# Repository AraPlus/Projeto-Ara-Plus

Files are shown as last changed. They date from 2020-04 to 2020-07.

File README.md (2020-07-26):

# Projeto-Ara-Plus
Repositório de projeto de um AMBU automatizado desenvolvido por estudantes, pesquisadores e professores da Universidade Federal do ABC (UFABC) para substituir um ventilador pulmonar de forma emergencial nos casos de COVID-19. Este é um trabalho em desenvolvimento, e ainda não está apto para casos clínicos. Futuras atualizações devem ser lançadas em breve.

## Origem do Nome
O nome "Ara" vem do Tupi-Guarani e significa "ar". Portanto o nome Ara-Plus reune uma palava genuinamente brasileira com uma palavra do inglês reconhecida em todo o mundo, significando literalmente "mais ar".

## Descrição geral do sistema

### Requisitos

Conforme destacado pela AMIB – [Associação de Medicina Intensiva Brasileira]() – em sua nota técnica ["Nota técnica sobre características de aparelhos ventiladores artificiais no suporte ao paciente com COVID-19"](http://www.amib.org.br/fileadmin/user_upload/amib/2020/abril/26/Nota_te__cnica_sobre_caracteri__sticas_de_aparelhos_ventiladores_artificiais_no_suporte_ao_paciente_com_COVID-19.pdf) de 26 de abril de 2020 e que atualmente (29/05/2020) subsidia o [PROJETO DE LEI N° 2294, DE 2020, em tramitação no senado,](https://www25.senado.leg.br/web/atividade/materias/-/materia/142132): "No atual cenário de pandemia por COVID-19, diante de uma situação de exceção decorrente do grande número de pacientes com necessidade de ventilação mecânica, listamos abaixo as especificações MÍNIMAS que um ventilador mecânico deve apresentar para ventilar pacientes com COVID-19, em qualquer unidade (pronto socorro, UTI ou outras unidades). Essas características devem estar presentes, independentemente de o equipamento ser ventilador de transporte ou não, ser novo ou reformado:
1. MODOS VCV e/ou PCV;
2. CONTROLE DE DELTA DE PRESSÃO (SOBRE A PEEP) NO MODO PCV (DE 5 A 30 cmH2O) E CONTROLE DE VOLUME CORRENTE INSPIRADO NO MODO VCV (de 50 A 700 ML);
3. CONTROLE DE FiO2 (21 a 100%);
4. PEEP (0 ATE 20 cm H2O);
5. CONTROLE DE TEMPO INSPIRATÓRIO (NO MODO PCV) EM SEGUNDOS (0,3 - 2,0 S) E FLUXO INSPIRATÓRIO (NO MODO VCV) - ATÉ 70L/MIN;
6. CONTROLE DE FREQUÊNCIA RESPIRATÓRIA - 8 a 40 RPM;
7. MEDIDA DE PRESSÃO DE VIAS AÉREAS (MANÔMETRO ANALÓGICO OU DIGITAL);
8. MEDIDA DE VOLUME CORRENTE EXPIRADO SEMPRE QUE POSSÍVEL;
9. ALARME DE PRESSÃO MÁXIMA EM VIAS ÁEREAS, VAZAMENTO E QUEDA DE REDE DE GASES;
10. POSSIBILIDADE DE ANEXAR FILTRO TIPO HEPA DE ALTA CAPACIDADE (N99 OU N100) NO RAMO EXPIRATÓRIO;
11. SE POSSÍVEL, POSSUIR BATERIA COM PELO MENOS 2 HORAS DE CAPACIDADE."

## Lista de Material
Descrição de todas os materiais e peças usados no Ara Plus separados por categorias:

### Partes Eletrônicas

**Diagrama elétrico do acionamento**
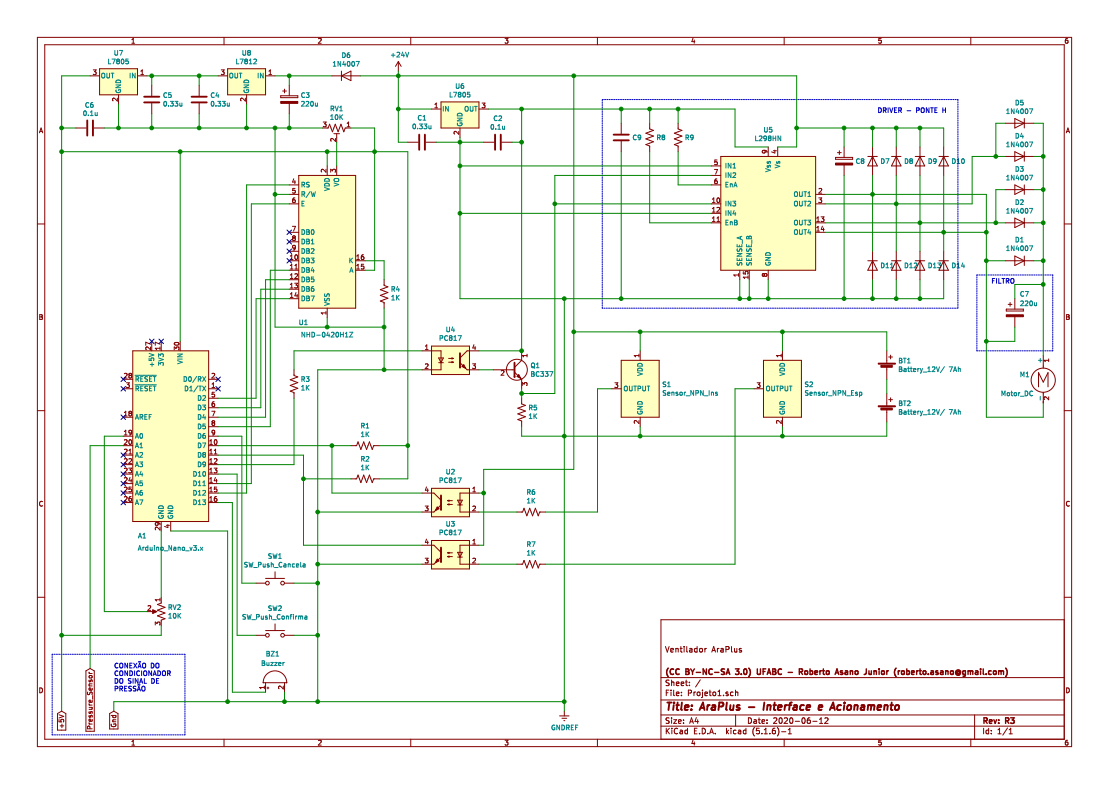
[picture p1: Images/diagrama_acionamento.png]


**Lista de materiais do acionamento**
 | Referência | Quantidade | Especificação | 
 | --------------- | --------------- | --------------- | 
 | A1 | 1 | Arduino Nano v3.x | 
 | BT1, BT2 | 2 | Bateria 12V/ 7Ah | 
 | BZ1 | 1 | Buzzer ativo 5V | 
 | C1, C4, C5 | 3 | Capacitor 0.33uF | 
 | C2, C6 | 2 | Capacitor 0.1uF | 
 | C3, C7 | 2 | Capacitor 220u
 | D1, D2, D3, D4, D5, D6, D7 | 7 | Diodo 1N4007 | 
 | M1 | 1 | Motor DC | 
 | Q1 | 1 | Transistor BC337 | 
 | RV1 | 1 | Trimpot 10K | 
 | RV2 | 1 | Potenciômetro 10K | 
 | R1, R2, R3, R4, R5, R6, R7 | 7 | Resistor 1K | 
 | S1, S2 | 2 | Sensor Indutivo NPN 12mm | 
 | SW1, SW2 | 2 | Acionador Push Buttom | 
 | U1 | 1 | Display alfanumérico 4 x 20 NHD-0420H1Z | 
 | U2, U3, U4 | 3 | Optoacoplador PC817 | 
 | U5 | 1 | Módulo Ponte H - L298N | 
 | U6, U7 | 2 | Regulador L7805 | 
 | U8 | 1 | Regulador L7812 | 
 | +24V | 1 | Fonte 24V - 5A |

### Partes Mecânicas
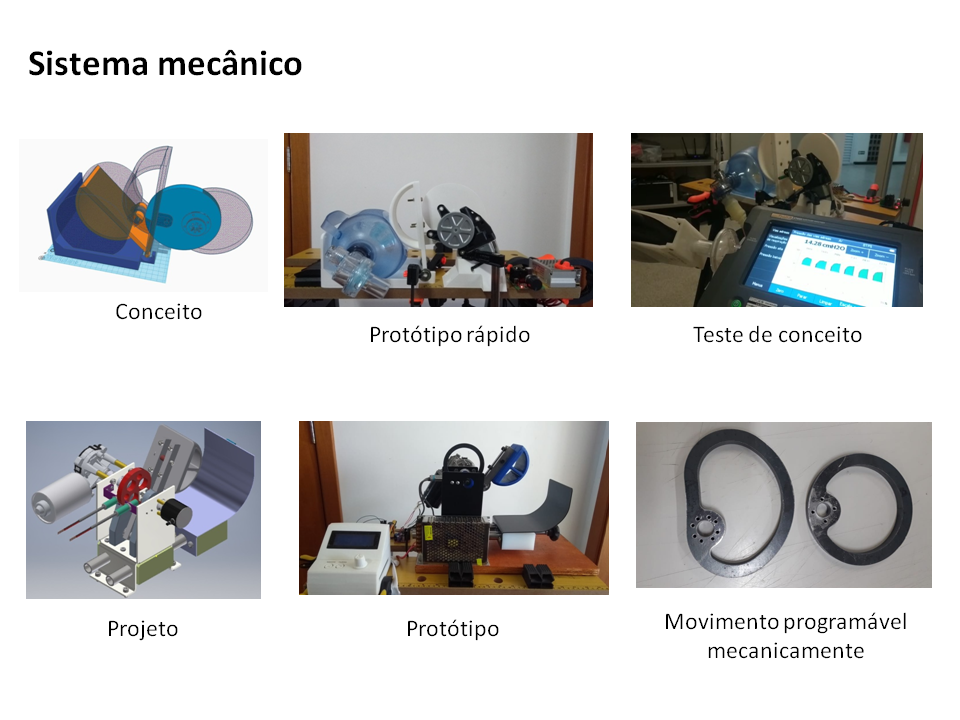
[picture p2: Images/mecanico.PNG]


## Desenhos de Fabricação / Arquivos de CAD
As informações sobre os desenhos de fabricação das partes mecânicas do AraPlus encontram-se [aqui](desenhos/DESENHOS.md)

### Partes médicas

Propostas em estudo do circuito pneumático:

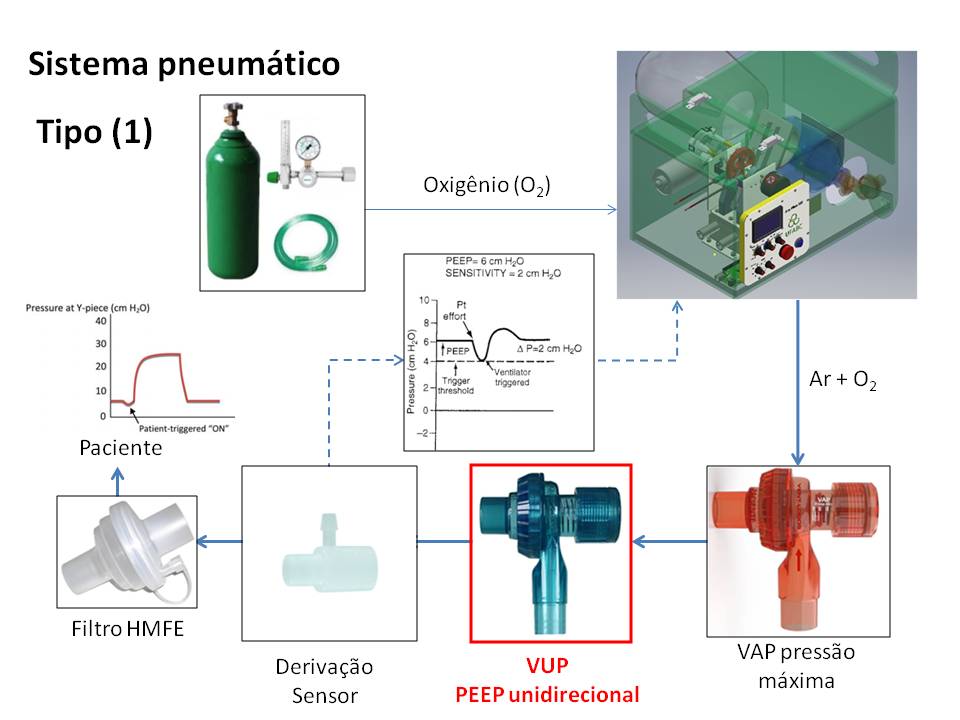
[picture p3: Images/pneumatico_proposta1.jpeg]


**Tipo 1 - Com válvula VUP**

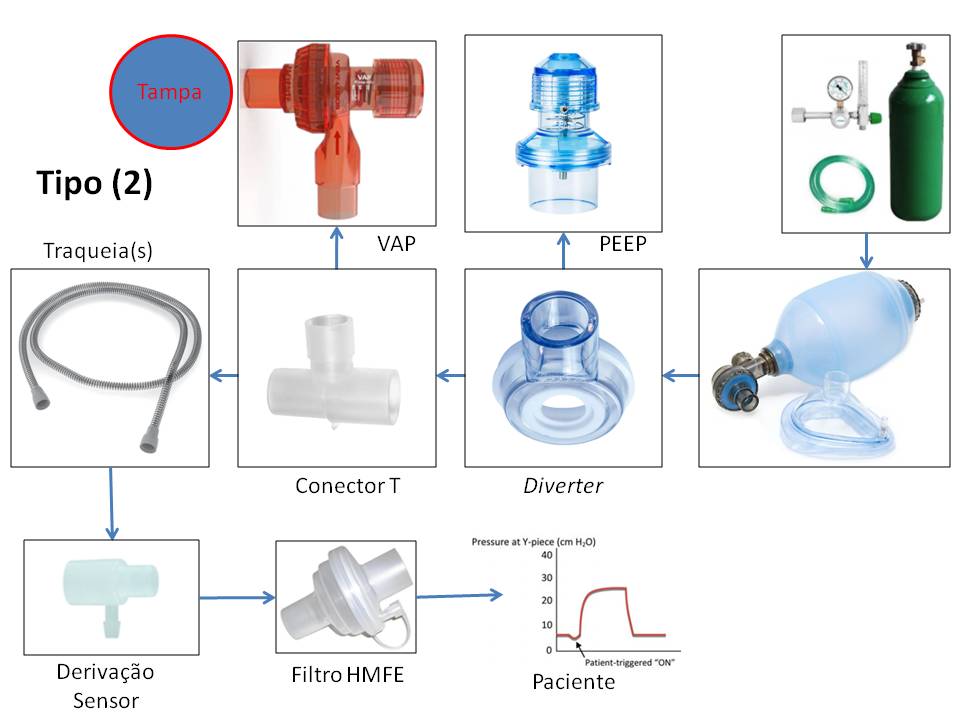
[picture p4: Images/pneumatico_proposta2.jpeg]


**Tipo 2 - Com Diverter e a válvula VAP tampada de um lado**

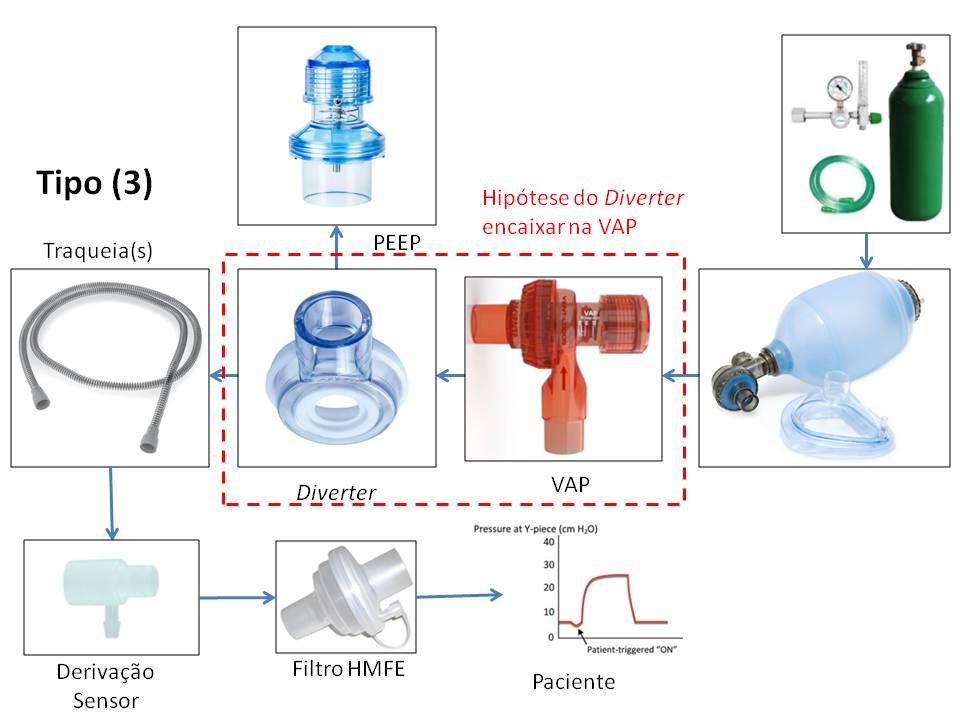
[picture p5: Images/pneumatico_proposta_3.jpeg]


**Tipo 3 - Com a hipótese do *Diverter* para encaixe na VAP**

## Fotos

Acionamento Mecânico

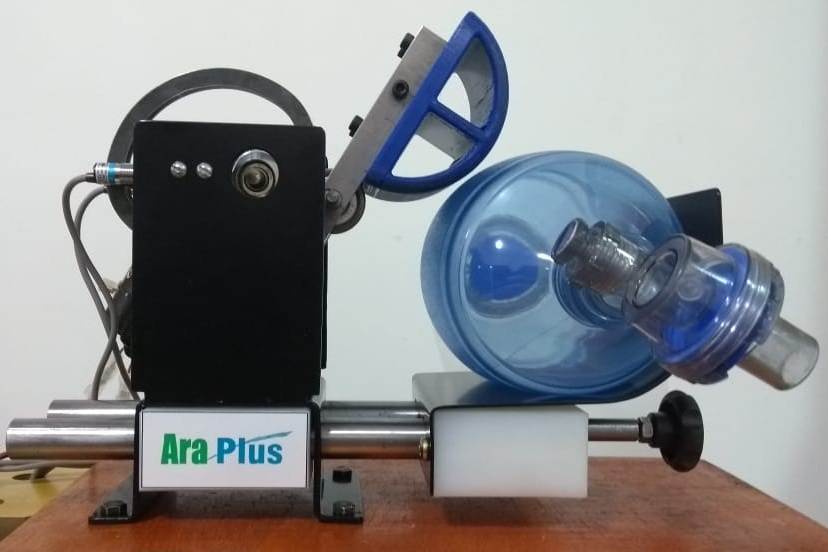
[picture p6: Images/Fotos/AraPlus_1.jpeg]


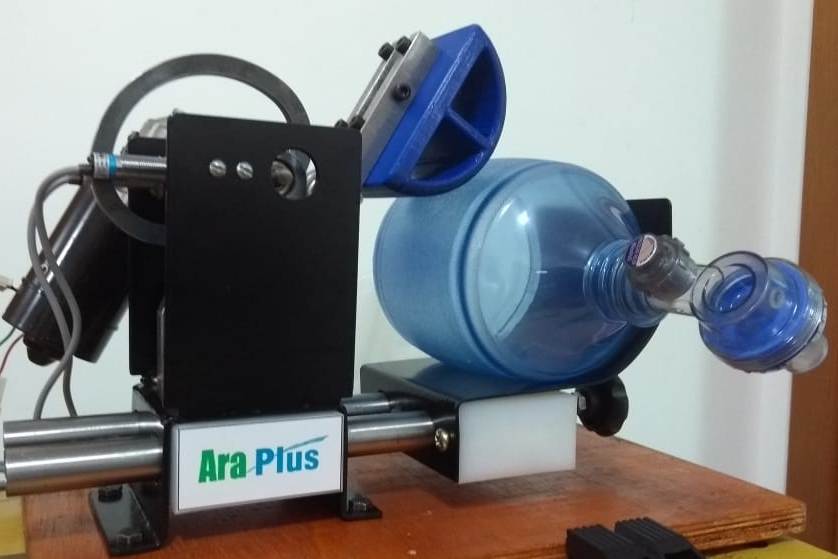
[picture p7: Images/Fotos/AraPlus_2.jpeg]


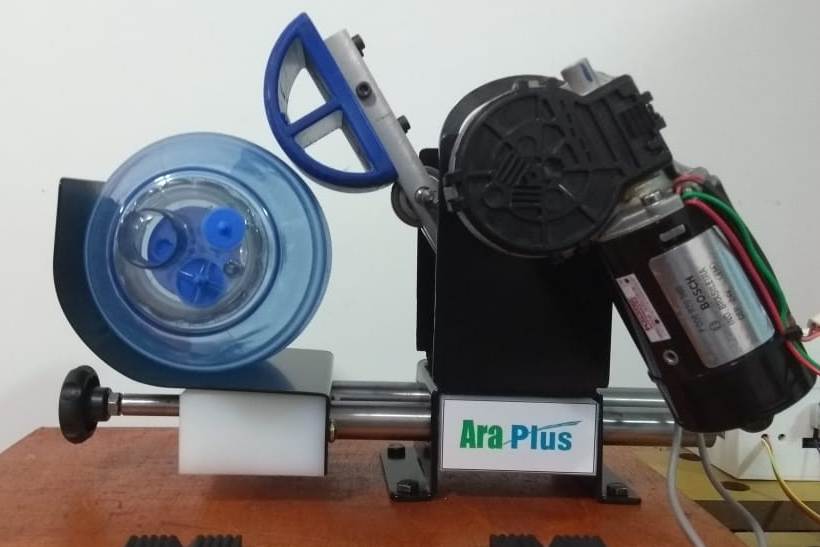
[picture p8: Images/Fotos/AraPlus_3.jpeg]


 ## Descrição dos Testes Funcionais de Bancada (in vitro)
 
**1) Levantamento da Relação PEEP x Pressão Expiratória Máxima (Vál. VAP) x Freq. Respiratória x Volume Inspirado**

**2) Levantamento da freqüência de operação, e relações Ti:Te possíveis**

Avaliar desempenho dinâmico do motor e capacidade de controle de velocidade para ajuste dos tempos.

**3) Levantamento da Relação de FIO2 e Fluxo de Oxigênio (Fluxímetro de parede)**

Referência:
GODOY, Armando Carlos Franco de; VIEIRA, Ronan José. Comparação da FiO2 fornecida por sete modelos de sistema balão-máscara auto-inflável. Rev. Bras. Anestesiol.,  Campinas ,  v. 59, n. 1, p. 21-27,  Feb.  2009 .   Available from <[http://www.scielo.br/scielo.php?script=sci_arttext&pid=S0034-70942009000100004&lng=en&nrm=iso]>. access on  22  June  2020.  [https://doi.org/10.1590/S0034-70942009000100004].

**4) Levantamento da relação de tempos determinadas mecanicamente e pelas curvas de pressão pneumática**

Averiguar para diversas condições se os tempos Ti e Te medidos pelos sensores posicionados no eixo do motor corresponde aos tempos de Ti e Te medidos pela curva de pressão/ fluxo pneumático.

**5) Calibração Estática do Sensor de Pressão**

Levantar curva de pressão medida pelo sensor MPS20N0040d comparando com uma medição de pressão estática (com manômetro U ou manômetro analógico)

**6) Calibração Dinâmica (valores simulados)**

Comparação das curvas de pressão e volume obtidas com um sensor de reverência (Analisador de Gases Fluke VT650) com as curvas de pressão obtidas com o simulador https://girardi.blumenau.ufsc.br/sdvm/, para os mesmos parâmetros ventilatórios.

**7) Calibração Dinâmica (valores experimentais)**

Comparação das curvas de pressão com um sensor de reverência, com as curvas de pressão efetivamente medidas com o sensor MPS20N0040d. Obs: o analisador  Fluke aparentemente só exporta com uma frequência de amostragem máxima de 1Hz, o que não dá uma boa resolução das curvas. A solução seria usar o sensor Magnamed Ventmeter que tem interface RS232.

**8) Determinação do procedimento de calibração do sensor de pressão embarcado**

Estabelecer rotina de calibração do sensor de pressão. Procedimento de manutenção.

## Cronologia do Desenvolvimento
Data dos principais marcos do desenvolvimento do Ara-Plus

- 25/07/2020: Proposta conceitual tecnológica para estimar FiO2 ([detalhes](./Titulação_FIO2/FIO2.md)) 
- 10/07/2020: Decidida alteração do tipo de motor e projeto em função dos novos requisitos para uso clínico em combate à COVID-19 e dos resultados dos testes em laboratório ([detalhes](./testes_de_bancada/Resultados_Motor_DC.md)) 
- 17/06/2020: Início dos testes do circuito médico/pneumático
- 07/06/2020: Finalizada a montagem do circuito de acionamento e controle
- 06/06/2020: Elaboração das propostas de circuito pneumático
- 03/03/2020: Correções a aprimoramento do acionador mecânico
- 01/06/2020: Submissão do projeto para [edital IEEE](https://hac.ieee.org/funding-opportunities/covid-19-projects/)
- 31/05/2020: Calibração do circuito condicionador do transdutor de pressão MPS20
- 18/05/2020: Finalizada a montagem do projeto mecânico
- 27/04/2020: Desenho mecânico do protótipo para testes
- 09/04/2019: Início do desenvolvimento do software
- 06/04/2020: Submissão de projeto para edital interno de pesquisa
- 03/04/2020: Testes do protótipo conceitual
- 23/03/2020: Publicação do projeto conceitual ([Tinkercad](https://www.tinkercad.com/things/d3R13CpPf5m ))
- 19/03/2020: Formação do grupo de desenvolvimento 
- 16/03/2020: Início da suspensão das aulas na UFABC devido à pandemia
- 11/03/2020: Declaração de pandemia de COVID-19 pela OMS

## Financiamento
Este projeto foi contemplado pela chamada Interna de Prospecção Para Apoio a Projetos e Ações de Pesquisa, Inovação, Extensão e Extensão Tecnológica para o Enfrentamento da Emergência de Saúde Pública Decorrente da COVID-19 da reitoria da UFABC.
Valor do financiamento: R$ 8.957,60

[http://www.ufabc.edu.br/images/reitoria/documentos/edital-42_2020-chamada-de-propostas-covid-19.pdf]

Esta projeto também conta com o apoio financeiro do IEEE HAC e IEEE SIGHT que apresentou um edital em resposta à pandemia da COVID-19.

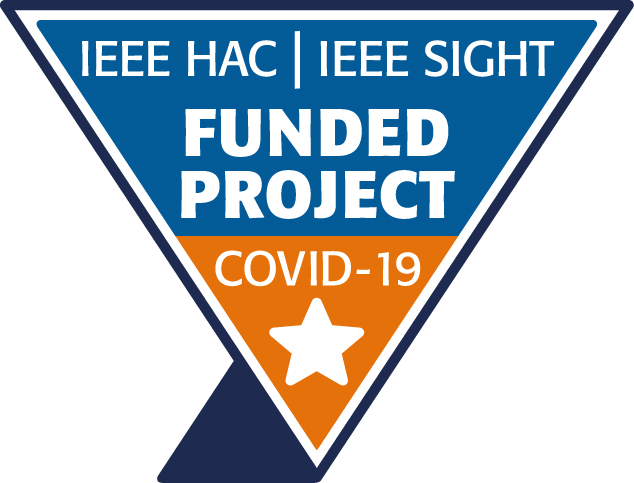
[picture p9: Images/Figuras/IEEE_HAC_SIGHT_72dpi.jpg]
[https://hac.ieee.org/funding-opportunities/covid-19-projects/]  

Maiores informações sobre editais com os respectivos projetos submetidos encontram-se [aqui](editais/EDITAIS.md).

## Lista de Compras 
Tabela com todos os itens adquiridos para o desenvolvimento deste projeto

Data da Compra  | Descrição do item | Quem comprou? | Origem do Recurso | Valor (R$)  
--------------- | ------------------|---------------|-------------------|------------
01/01/1900 | Exemplo 1 | Olavo | Do bolso | 10,00 
02/01/1900 | Exemplo 2 | Fulano | Edital UFABC | 20,00 
03/01/1900 | Exemplo 3 | Cicrano | Doação empresa XX | 0,00 

## Glossário
Aqui encontram-se os principais termos e siglas usados no desenvolvimento deste projeto juntamente com o seu significado:
- AMBU (Artificial Manual Breathing Unit) é que uma Unidade Manual de Respiração Artificial, ou Reanimador Manual [referência](https://enfermagemilustrada.com/unidade-manual-de-respiracao-artificial-ambu-reanimador-manual/)
- Filtro HEPA  = High Efficiency Particulate Air 
- Filtro HMEF
- Filtro Humidificador
- FiO2 - Fração Inspirada de Oxigênio ([molar ou em volume](https://en.wikipedia.org/wiki/Fraction_of_inspired_oxygen))
- PEEP (Positive end-expiratory pressure) Pressão Positiva ao Final da Expiração [referência](https://en.wikipedia.org/wiki/Positive_end-expiratory_pressure)
- Válvula VAP (?)
- Válvula VUP
- PCV = Pressão Controlada Ciclado a Tempo;
- VCV = Volume Controlado ou Ciclado a Volume;
- PSV = Ventilação com Pressão de Suporte HEPA
- FiO2 = Fração Inspirada de Oxigênio,

## Equipe
- [Olavo Luppi Silva](http://ebm.ufabc.edu.br/docentes/olavo-luppi/) - Professor Adjunto - Eng. Biomédica/UFABC
- [Erick Dario León Bueno de Camargo](http://ebm.ufabc.edu.br/docentes/erickleon/) - Professor Adjunto - Eng. Biomédica/UFABC
- [Harki Tanaka](http://ebm.ufabc.edu.br/docentes/harki-tanaka/) - Professor Adjunto - Eng. Biomédica/UFABC
- Hermann Windisch Neto - Aluno de doutorado no programa de [Biotecnociência/UFABC](http://propg.ufabc.edu.br/biotecnociencia/)
- Victor Allisson da Silva - Aluno da graduação da Engenharia Biomédica/UFABC
- Danilo Luna Campos - Aluno da graduação da Engenharia Biomédica
- Paulo Rodrigues - Aluno especial de mestrado no [PPGEBM](http://ebm.ufabc.edu.br/pos-graduacao/ppgebm/)
- Ana Tércia Lacerda de Araújo - Aluna de graduação do BC&T
- Ivan Correia Lima Coqueiro - Aluno de graduação do BC&T
- Jaqueline Badanai - Aluna de mestrado da [PPGEBM](http://ebm.ufabc.edu.br/pos-graduacao/ppgebm/)
- Danilo Buchdid - Colaborador externo
- Roberto Asano Junior - Pesquisador Pós-Doc - [Energia/UFABC](http://pgene.ufabc.edu.br)
- Edson Rodrigues - Aluno de mestrado no [PPGEBM](http://ebm.ufabc.edu.br/pos-graduacao/ppgebm/)
- [Patrícia Teixeira Leite Asano](http://cecs.ufabc.edu.br/index.php/docentes/contatos/23-docentes/143-patricia-teixeira-leite-asano.html) - Professor Associado - Eng. Energia/UFABC

## Parceiros
 - FMABC: testes clínicos
 - Prefer: usinagem 
 - Ventisilva: manufatura
  
## Agradecimentos
 - Dcryl Design em Acrílico (Campinas)
 - IEEE R9 Jt. Chapter Energy Industry Connections
 - Instituto Mauá de Tecnologia
 - Rotary-International

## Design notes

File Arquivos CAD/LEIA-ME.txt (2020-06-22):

%---------------------------projeto ARA PLUS ------------------------------%
%-------------------VERSÃO V03 - VENTILADOR PULMONAR UFABC ----------------%
%--------------------------------------------------------------------------%

Esta é a versão V3 do protótipo de ventilador Pulmonar. Próximas atualizações 
serão realizadas.

UPDATES:

-Acionador de AMBU através de motor Bosch 24V

Para mais detalhes verifique o repositório Projeto-Ara-Plus

Updated on: 21-06-2020

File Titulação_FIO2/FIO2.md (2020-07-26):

# Proposta de estimador de FI02 com 3 termometros

Estimar a relação de massas (e volume correlacionado) através da medição de temperaturas dos gases que entram no AMBU e o resultante da mistura.

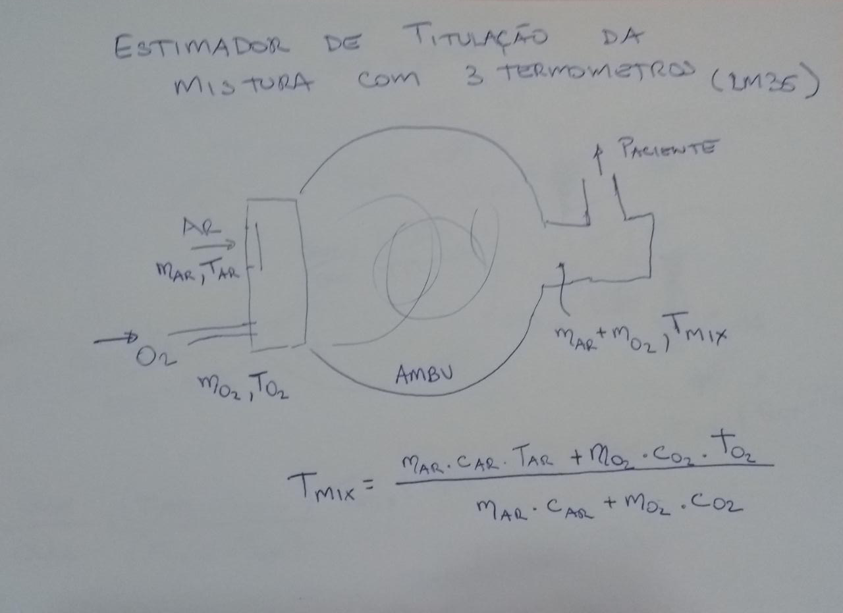
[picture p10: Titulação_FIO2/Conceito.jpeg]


## Referências para verificação:

Godoy ACF, Vieira RJ, Neto RJV. Oxygen outflow delivered by manually operated self-inflating resuscitation bags in patients breathing spontaneously. J Bras Pneumol. 2008;34(4):212-216. Disponível em: [https://www.jornaldepneumologia.com.br/detalhe_artigo.asp?id=385]

Godoy, Armando Carlos Franco de, & Vieira, Ronan José. (2009). Comparação da FiO2 fornecida por sete modelos de sistema balão-máscara auto-inflável. Revista Brasileira de Anestesiologia, 59(1), 21-27.  Disponível em: [https://doi.org/10.1590/S0034-70942009000100004] ou [https://www.scielo.br/scielo.php?script=sci_arttext&pid=S0034-70942009000100004]

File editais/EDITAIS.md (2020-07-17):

# EDITAIS

Nesta páginas estão os editais que o Ventilador AraPlus concorreu bem como os projetos submeditos para cada um dos editais.

- [Edital interno UFABC](editais/Edital-42_2020-chamada-de-propostas-covid-19.pdf) (prazo de submissão: 05/04/2020): status **aprovado**.
Veja [aqui](projetos/Projeto_VentiladorPulmonar_AraPlus_edital_UFABC.pdf) o projeto submetido para este edital

- [Edital IEEE](Edital_IEEE-HAC-Projects-CfP-COVID-19-10-April-2020-FINAL.pdf) (prazo de submissão: 01/06/2020): status **aprovado** Veja [aqui](projetos/Projeto_submetido_IEEE-HAC.pdf) o projeto submetido para este edital

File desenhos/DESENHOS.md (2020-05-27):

# DESENHOS

Os desenhos de fabricação das partes mecânicas do AraPlus, em formato .pdf encontram-se em aqui.
Os arquivos de CAD, em formato .dwg, relativos aos desenhos de fabricação encontram-se aqui.

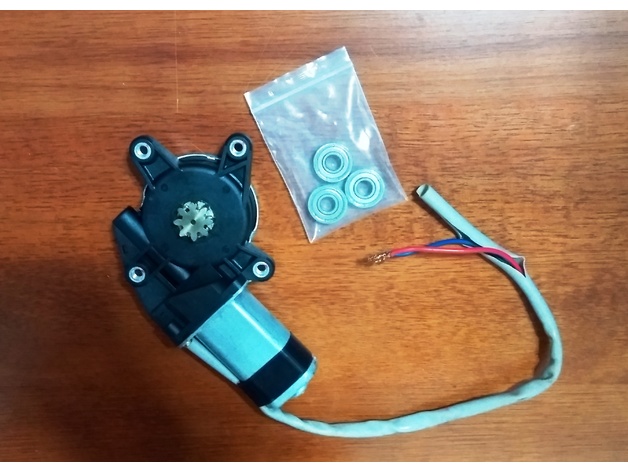
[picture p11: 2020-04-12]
R3/Respirator_COVID19_Concept/images/Car_Window_Motor_Bearings_608.jpg

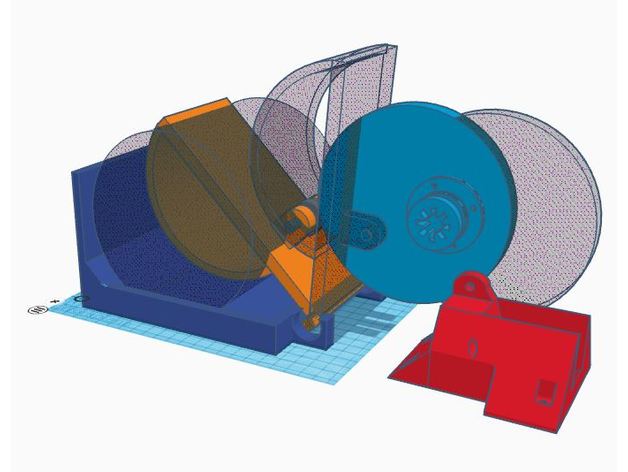
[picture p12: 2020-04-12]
R3/Respirator_COVID19_Concept/images/Fig_two_positions_R2.JPG

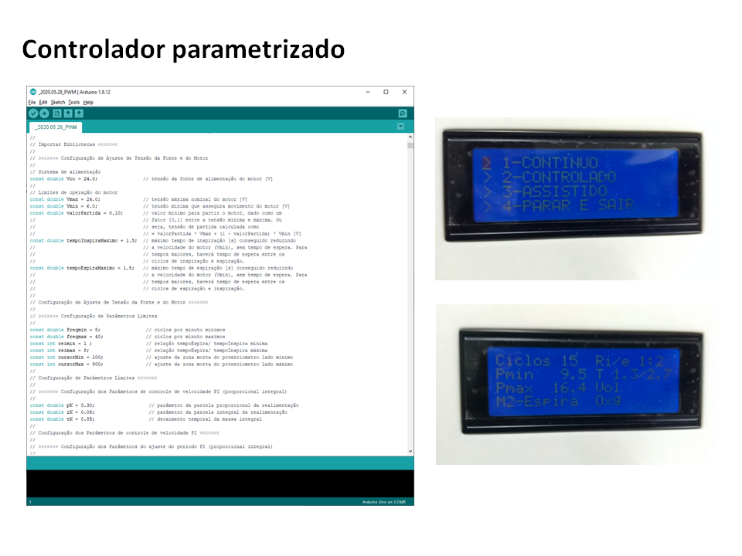
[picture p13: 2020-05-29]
Images/controlador.PNG

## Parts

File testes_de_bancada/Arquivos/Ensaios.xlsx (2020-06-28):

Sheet: Medições
# | Pulmão | Posição | Ciclos | Relação | Mola | PEEP | VAP | Tins | Tesp | P(display) | P(Fluke) | Vol | Obs.
1 | Mindray (P&B) | 1 | 18 | 1:2 | UP | 5 | 10
2 | Mindray (P&B) | 1 | 18 | 1:2 | UP | 5 | 20
3 | Mindray (P&B) | 1 | 18 | 1:2 | UP | 5 | 30
4 | Mindray (P&B) | 1 | 18 | 1:2 | UP | 5 | 40
5 | Mindray (P&B) | 1 | 18 | 1:2 | UP | 10 | 10
6 | Mindray (P&B) | 1 | 18 | 1:2 | UP | 10 | 20
7 | Mindray (P&B) | 1 | 18 | 1:2 | UP | 10 | 30
8 | Mindray (P&B) | 1 | 18 | 1:2 | UP | 10 | 40
9 | Mindray (P&B) | 1 | 18 | 1:2 | UP | 15 | 10
10 | Mindray (P&B) | 1 | 18 | 1:2 | UP | 15 | 20
11 | Mindray (P&B) | 1 | 18 | 1:2 | UP | 15 | 30
12 | Mindray (P&B) | 1 | 18 | 1:2 | UP | 15 | 40
13 | Mindray (P&B) | 1 | 18 | 1:2 | UP | 20 | 10
14 | Mindray (P&B) | 1 | 18 | 1:2 | UP | 20 | 20
15 | Mindray (P&B) | 1 | 18 | 1:2 | UP | 20 | 30
16 | Mindray (P&B) | 1 | 18 | 1:2 | UP | 20 | 40
17 | Mindray (P&B) | 1 | 18 | 1:2 | DOWN | 20 | 40
18 | Mindray (P&B) | 1 | 18 | 1:2 | DOWN | 20 | 30
19 | Mindray (P&B) | 1 | 18 | 1:2 | DOWN | 20 | 20
20 | Mindray (P&B) | 1 | 18 | 1:2 | DOWN | 20 | 10
21 | Mindray (P&B) | 1 | 18 | 1:2 | DOWN | 15 | 40
22 | Mindray (P&B) | 1 | 18 | 1:2 | DOWN | 15 | 30
23 | Mindray (P&B) | 1 | 18 | 1:2 | DOWN | 15 | 20
24 | Mindray (P&B) | 1 | 18 | 1:2 | DOWN | 15 | 10
25 | Mindray (P&B) | 1 | 18 | 1:2 | DOWN | 10 | 40
26 | Mindray (P&B) | 1 | 18 | 1:2 | DOWN | 10 | 30
27 | Mindray (P&B) | 1 | 18 | 1:2 | DOWN | 10 | 20
28 | Mindray (P&B) | 1 | 18 | 1:2 | DOWN | 10 | 10
29 | Mindray (P&B) | 1 | 18 | 1:2 | DOWN | 5 | 40
30 | Mindray (P&B) | 1 | 18 | 1:2 | DOWN | 5 | 30
31 | Mindray (P&B) | 1 | 18 | 1:2 | DOWN | 5 | 20
32 | Mindray (P&B) | 1 | 18 | 1:2 | DOWN | 5 | 10
33 | Mindray (P&B) | 1 | 32 | 1:1 | UP | 5 | 10
34 | Mindray (P&B) | 1 | 32 | 1:1 | UP | 5 | 20
35 | Mindray (P&B) | 1 | 32 | 1:1 | UP | 5 | 30
36 | Mindray (P&B) | 1 | 32 | 1:1 | UP | 5 | 40
37 | Mindray (P&B) | 1 | 32 | 1:1 | UP | 10 | 10
38 | Mindray (P&B) | 1 | 32 | 1:1 | UP | 10 | 20
39 | Mindray (P&B) | 1 | 32 | 1:1 | UP | 10 | 30
40 | Mindray (P&B) | 1 | 32 | 1:1 | UP | 10 | 40
41 | Mindray (P&B) | 1 | 32 | 1:1 | UP | 15 | 10
42 | Mindray (P&B) | 1 | 32 | 1:1 | UP | 15 | 20
43 | Mindray (P&B) | 1 | 32 | 1:1 | UP | 15 | 30
44 | Mindray (P&B) | 1 | 32 | 1:1 | UP | 15 | 40
45 | Mindray (P&B) | 1 | 32 | 1:1 | UP | 20 | 10
46 | Mindray (P&B) | 1 | 32 | 1:1 | UP | 20 | 20
47 | Mindray (P&B) | 1 | 32 | 1:1 | UP | 20 | 30
48 | Mindray (P&B) | 1 | 32 | 1:1 | UP | 20 | 40
49 | Mindray (P&B) | 1 | 32 | 1:1 | DOWN | 20 | 40
50 | Mindray (P&B) | 1 | 32 | 1:1 | DOWN | 20 | 30
51 | Mindray (P&B) | 1 | 32 | 1:1 | DOWN | 20 | 20
52 | Mindray (P&B) | 1 | 32 | 1:1 | DOWN | 20 | 10
53 | Mindray (P&B) | 1 | 32 | 1:1 | DOWN | 15 | 40
54 | Mindray (P&B) | 1 | 32 | 1:1 | DOWN | 15 | 30
55 | Mindray (P&B) | 1 | 32 | 1:1 | DOWN | 15 | 20
56 | Mindray (P&B) | 1 | 32 | 1:1 | DOWN | 15 | 10
57 | Mindray (P&B) | 1 | 32 | 1:1 | DOWN | 10 | 40
58 | Mindray (P&B) | 1 | 32 | 1:1 | DOWN | 10 | 30
59 | Mindray (P&B) | 1 | 32 | 1:1 | DOWN | 10 | 20
60 | Mindray (P&B) | 1 | 32 | 1:1 | DOWN | 10 | 10
61 | Mindray (P&B) | 1 | 32 | 1:1 | DOWN | 5 | 40
62 | Mindray (P&B) | 1 | 32 | 1:1 | DOWN | 5 | 30
63 | Mindray (P&B) | 1 | 32 | 1:1 | DOWN | 5 | 20
64 | Mindray (P&B) | 1 | 32 | 1:1 | DOWN | 5 | 10
65 | Mindray (P&B) | 1 | 11 | 1:4 | UP | 5 | 10
66 | Mindray (P&B) | 1 | 11 | 1:4 | UP | 5 | 20
67 | Mindray (P&B) | 1 | 11 | 1:4 | UP | 5 | 30
68 | Mindray (P&B) | 1 | 11 | 1:4 | UP | 5 | 40
69 | Mindray (P&B) | 1 | 11 | 1:4 | UP | 10 | 10
70 | Mindray (P&B) | 1 | 11 | 1:4 | UP | 10 | 20
71 | Mindray (P&B) | 1 | 11 | 1:4 | UP | 10 | 30
72 | Mindray (P&B) | 1 | 11 | 1:4 | UP | 10 | 40
73 | Mindray (P&B) | 1 | 11 | 1:4 | UP | 15 | 10
74 | Mindray (P&B) | 1 | 11 | 1:4 | UP | 15 | 20
75 | Mindray (P&B) | 1 | 11 | 1:4 | UP | 15 | 30
76 | Mindray (P&B) | 1 | 11 | 1:4 | UP | 15 | 40
77 | Mindray (P&B) | 1 | 11 | 1:4 | UP | 20 | 10
78 | Mindray (P&B) | 1 | 11 | 1:4 | UP | 20 | 20
79 | Mindray (P&B) | 1 | 11 | 1:4 | UP | 20 | 30
80 | Mindray (P&B) | 1 | 11 | 1:4 | UP | 20 | 40
81 | Mindray (P&B) | 1 | 11 | 1:4 | DOWN | 20 | 40
82 | Mindray (P&B) | 1 | 11 | 1:4 | DOWN | 20 | 30
83 | Mindray (P&B) | 1 | 11 | 1:4 | DOWN | 20 | 20
84 | Mindray (P&B) | 1 | 11 | 1:4 | DOWN | 20 | 10
85 | Mindray (P&B) | 1 | 11 | 1:4 | DOWN | 15 | 40
86 | Mindray (P&B) | 1 | 11 | 1:4 | DOWN | 15 | 30
87 | Mindray (P&B) | 1 | 11 | 1:4 | DOWN | 15 | 20
88 | Mindray (P&B) | 1 | 11 | 1:4 | DOWN | 15 | 10
89 | Mindray (P&B) | 1 | 11 | 1:4 | DOWN | 10 | 40
90 | Mindray (P&B) | 1 | 11 | 1:4 | DOWN | 10 | 30
91 | Mindray (P&B) | 1 | 11 | 1:4 | DOWN | 10 | 20
92 | Mindray (P&B) | 1 | 11 | 1:4 | DOWN | 10 | 10
93 | Mindray (P&B) | 1 | 11 | 1:4 | DOWN | 5 | 40
94 | Mindray (P&B) | 1 | 11 | 1:4 | DOWN | 5 | 30
95 | Mindray (P&B) | 1 | 11 | 1:4 | DOWN | 5 | 20
96 | Mindray (P&B) | 1 | 11 | 1:4 | DOWN | 5 | 10 |  |  |  |  |  | Checar relevância do sentido UP/ DOWN na atuação das válvulas
97 | Mindray (P&B) | 1 | 28 | 1:1 | UP | 5 | 10
98 | Mindray (P&B) | 1 | 28 | 1:1 | UP | 5 | 20
99 | Mindray (P&B) | 1 | 28 | 1:1 | UP | 5 | 30
100 | Mindray (P&B) | 1 | 28 | 1:1 | UP | 5 | 40
101 | Mindray (P&B) | 1 | 28 | 1:1 | UP | 10 | 10
102 | Mindray (P&B) | 1 | 28 | 1:1 | UP | 10 | 20
103 | Mindray (P&B) | 1 | 28 | 1:1 | UP | 10 | 30
104 | Mindray (P&B) | 1 | 28 | 1:1 | UP | 10 | 40
105 | Mindray (P&B) | 1 | 28 | 1:1 | UP | 15 | 10
106 | Mindray (P&B) | 1 | 28 | 1:1 | UP | 15 | 20
107 | Mindray (P&B) | 1 | 28 | 1:1 | UP | 15 | 30
108 | Mindray (P&B) | 1 | 28 | 1:1 | UP | 15 | 40
109 | Mindray (P&B) | 1 | 28 | 1:1 | UP | 20 | 10
110 | Mindray (P&B) | 1 | 28 | 1:1 | UP | 20 | 20
111 | Mindray (P&B) | 1 | 28 | 1:1 | UP | 20 | 30
112 | Mindray (P&B) | 1 | 28 | 1:1 | UP | 20 | 40
113 | Mindray (P&B) | 1 | 23 | 1:1 | DOWN | 20 | 40
114 | Mindray (P&B) | 1 | 23 | 1:1 | DOWN | 20 | 30
115 | Mindray (P&B) | 1 | 23 | 1:1 | DOWN | 20 | 20
116 | Mindray (P&B) | 1 | 23 | 1:1 | DOWN | 20 | 10
117 | Mindray (P&B) | 1 | 23 | 1:1 | DOWN | 15 | 40
118 | Mindray (P&B) | 1 | 23 | 1:1 | DOWN | 15 | 30
119 | Mindray (P&B) | 1 | 23 | 1:1 | DOWN | 15 | 20
120 | Mindray (P&B) | 1 | 23 | 1:1 | DOWN | 15 | 10
121 | Mindray (P&B) | 1 | 23 | 1:1 | DOWN | 10 | 40
122 | Mindray (P&B) | 1 | 23 | 1:1 | DOWN | 10 | 30
123 | Mindray (P&B) | 1 | 23 | 1:1 | DOWN | 10 | 20
124 | Mindray (P&B) | 1 | 23 | 1:1 | DOWN | 10 | 10
125 | Mindray (P&B) | 1 | 23 | 1:1 | DOWN | 5 | 40
126 | Mindray (P&B) | 1 | 23 | 1:1 | DOWN | 5 | 30
127 | Mindray (P&B) | 1 | 23 | 1:1 | DOWN | 5 | 20
128 | Mindray (P&B) | 1 | 23 | 1:1 | DOWN | 5 | 10
129 | Mindray (P&B) | 1 | 23 | 1:2 | UP | 5 | 10
130 | Mindray (P&B) | 1 | 23 | 1:2 | UP | 5 | 20
131 | Mindray (P&B) | 1 | 23 | 1:2 | UP | 5 | 30
132 | Mindray (P&B) | 1 | 23 | 1:2 | UP | 5 | 40
133 | Mindray (P&B) | 1 | 23 | 1:2 | UP | 10 | 10
134 | Mindray (P&B) | 1 | 23 | 1:2 | UP | 10 | 20
135 | Mindray (P&B) | 1 | 23 | 1:2 | UP | 10 | 30
136 | Mindray (P&B) | 1 | 23 | 1:2 | UP | 10 | 40
137 | Mindray (P&B) | 1 | 23 | 1:2 | UP | 15 | 10
138 | Mindray (P&B) | 1 | 23 | 1:2 | UP | 15 | 20
139 | Mindray (P&B) | 1 | 23 | 1:2 | UP | 15 | 30
140 | Mindray (P&B) | 1 | 23 | 1:2 | UP | 15 | 40
141 | Mindray (P&B) | 1 | 23 | 1:2 | UP | 20 | 10
142 | Mindray (P&B) | 1 | 23 | 1:2 | UP | 20 | 20
143 | Mindray (P&B) | 1 | 23 | 1:2 | UP | 20 | 30
144 | Mindray (P&B) | 1 | 23 | 1:2 | UP | 20 | 40
145 | Mindray (P&B) | 1 | 19 | 1:2 | DOWN | 20 | 40
146 | Mindray (P&B) | 1 | 19 | 1:2 | DOWN | 20 | 30
147 | Mindray (P&B) | 1 | 19 | 1:2 | DOWN | 20 | 20
148 | Mindray (P&B) | 1 | 19 | 1:2 | DOWN | 20 | 10
149 | Mindray (P&B) | 1 | 19 | 1:2 | DOWN | 15 | 40
150 | Mindray (P&B) | 1 | 19 | 1:2 | DOWN | 15 | 30
151 | Mindray (P&B) | 1 | 19 | 1:2 | DOWN | 15 | 20
152 | Mindray (P&B) | 1 | 19 | 1:2 | DOWN | 15 | 10
153 | Mindray (P&B) | 1 | 19 | 1:2 | DOWN | 10 | 40
154 | Mindray (P&B) | 1 | 19 | 1:2 | DOWN | 10 | 30
155 | Mindray (P&B) | 1 | 19 | 1:2 | DOWN | 10 | 20
156 | Mindray (P&B) | 1 | 19 | 1:2 | DOWN | 10 | 10
157 | Mindray (P&B) | 1 | 19 | 1:2 | DOWN | 5 | 40
158 | Mindray (P&B) | 1 | 19 | 1:2 | DOWN | 5 | 30
159 | Mindray (P&B) | 1 | 19 | 1:2 | DOWN | 5 | 20
160 | Mindray (P&B) | 1 | 19 | 1:2 | DOWN | 5 | 10
161 | Mindray (P&B) | 1 | 17 | 1:3 | UP | 12.5 | 25
162 | Mindray (P&B) | 1 | 17 | 1:3 | UP | 12.5 | 25
163 | Mindray (P&B) | 1 | 17 | 1:3 | UP | 12.5 | 25
164 | Mindray (P&B) | 1 | 17 | 1:3 | UP | 12.5 | 25
165 | Mindray (P&B) | 1 | 17 | 1:3 | UP | 12.5 | 25
166 | Mindray (P&B) | 1 | 17 | 1:3 | UP | 12.5 | 25
167 | Mindray (P&B) | 1 | 17 | 1:3 | UP | 12.5 | 25
168 | Mindray (P&B) | 1 | 17 | 1:3 | UP | 12.5 | 25
169 | Mindray (P&B) | 1 | 17 | 1:3 | UP | 12.5 | 25
170 | Mindray (P&B) | 1 | 17 | 1:3 | UP | 12.5 | 25
171 | Mindray (P&B) | 1 | 17 | 1:3 | UP | 12.5 | 25
172 | Mindray (P&B) | 1 | 17 | 1:3 | UP | 12.5 | 25
173 | Mindray (P&B) | 1 | 17 | 1:3 | UP | 12.5 | 25
174 | Mindray (P&B) | 1 | 17 | 1:3 | UP | 12.5 | 25
175 | Mindray (P&B) | 1 | 17 | 1:3 | UP | 12.5 | 25
176 | Mindray (P&B) | 1 | 17 | 1:3 | UP | 12.5 | 25
177 | Mindray (P&B) | 1 | 14 | 1:3 | DOWN | 12.5 | 25
178 | Mindray (P&B) | 1 | 14 | 1:3 | DOWN | 12.5 | 25
179 | Mindray (P&B) | 1 | 14 | 1:3 | DOWN | 12.5 | 25
180 | Mindray (P&B) | 1 | 14 | 1:3 | DOWN | 12.5 | 25
181 | Mindray (P&B) | 1 | 14 | 1:3 | DOWN | 12.5 | 25
182 | Mindray (P&B) | 1 | 14 | 1:3 | DOWN | 12.5 | 25
183 | Mindray (P&B) | 1 | 14 | 1:3 | DOWN | 12.5 | 25
184 | Mindray (P&B) | 1 | 14 | 1:3 | DOWN | 12.5 | 25
185 | Mindray (P&B) | 1 | 14 | 1:3 | DOWN | 12.5 | 25
186 | Mindray (P&B) | 1 | 14 | 1:3 | DOWN | 12.5 | 25
187 | Mindray (P&B) | 1 | 14 | 1:3 | DOWN | 12.5 | 25
188 | Mindray (P&B) | 1 | 14 | 1:3 | DOWN | 12.5 | 25
189 | Mindray (P&B) | 1 | 14 | 1:3 | DOWN | 12.5 | 25
190 | Mindray (P&B) | 1 | 14 | 1:3 | DOWN | 12.5 | 25
191 | Mindray (P&B) | 1 | 14 | 1:3 | DOWN | 12.5 | 25
192 | Mindray (P&B) | 1 | 14 | 1:3 | DOWN | 12.5 | 25
193 | Mindray (P&B) | 1 | 12 | 1:3 | UP | 12.5 | 25
194 | Mindray (P&B) | 1 | 12 | 1:3 | UP | 12.5 | 25
195 | Mindray (P&B) | 1 | 12 | 1:3 | UP | 12.5 | 25
196 | Mindray (P&B) | 1 | 12 | 1:3 | UP | 12.5 | 25
197 | Mindray (P&B) | 1 | 12 | 1:3 | UP | 12.5 | 25
198 | Mindray (P&B) | 1 | 12 | 1:3 | UP | 12.5 | 25
199 | Mindray (P&B) | 1 | 12 | 1:3 | UP | 12.5 | 25
200 | Mindray (P&B) | 1 | 12 | 1:3 | UP | 12.5 | 25
201 | Mindray (P&B) | 1 | 12 | 1:3 | UP | 12.5 | 25
202 | Mindray (P&B) | 1 | 12 | 1:3 | UP | 12.5 | 25
203 | Mindray (P&B) | 1 | 12 | 1:3 | UP | 12.5 | 25
204 | Mindray (P&B) | 1 | 12 | 1:3 | UP | 12.5 | 25
205 | Mindray (P&B) | 1 | 12 | 1:3 | UP | 12.5 | 25
206 | Mindray (P&B) | 1 | 12 | 1:3 | UP | 12.5 | 25
207 | Mindray (P&B) | 1 | 12 | 1:3 | UP | 12.5 | 25
208 | Mindray (P&B) | 1 | 12 | 1:3 | UP | 12.5 | 25
209 | Mindray (P&B) | 1 | 14 | 1:4 | DOWN | 12.5 | 25
210 | Mindray (P&B) | 1 | 14 | 1:4 | DOWN | 12.5 | 25
211 | Mindray (P&B) | 1 | 14 | 1:4 | DOWN | 12.5 | 25
212 | Mindray (P&B) | 1 | 14 | 1:4 | DOWN | 12.5 | 25
213 | Mindray (P&B) | 1 | 14 | 1:4 | DOWN | 12.5 | 25
214 | Mindray (P&B) | 1 | 14 | 1:4 | DOWN | 12.5 | 25
215 | Mindray (P&B) | 1 | 14 | 1:4 | DOWN | 12.5 | 25
216 | Mindray (P&B) | 1 | 14 | 1:4 | DOWN | 12.5 | 25
217 | Mindray (P&B) | 1 | 14 | 1:4 | DOWN | 12.5 | 25
218 | Mindray (P&B) | 1 | 14 | 1:4 | DOWN | 12.5 | 25
219 | Mindray (P&B) | 1 | 14 | 1:4 | DOWN | 12.5 | 25
220 | Mindray (P&B) | 1 | 14 | 1:4 | DOWN | 12.5 | 25
221 | Mindray (P&B) | 1 | 14 | 1:4 | DOWN | 12.5 | 25
222 | Mindray (P&B) | 1 | 14 | 1:4 | DOWN | 12.5 | 25
223 | Mindray (P&B) | 1 | 14 | 1:4 | DOWN | 12.5 | 25
224 | Mindray (P&B) | 1 | 14 | 1:4 | DOWN | 12.5 | 25
225 | Mindray (P&B) | 1 | 9 | 1:4 | UP | 12.5 | 25
226 | Mindray (P&B) | 1 | 9 | 1:4 | UP | 12.5 | 25
227 | Mindray (P&B) | 1 | 9 | 1:4 | UP | 12.5 | 25
228 | Mindray (P&B) | 1 | 9 | 1:4 | UP | 12.5 | 25
229 | Mindray (P&B) | 1 | 9 | 1:4 | UP | 12.5 | 25
230 | Mindray (P&B) | 1 | 9 | 1:4 | UP | 12.5 | 25
231 | Mindray (P&B) | 1 | 9 | 1:4 | UP | 12.5 | 25
232 | Mindray (P&B) | 1 | 9 | 1:4 | UP | 12.5 | 25
233 | Mindray (P&B) | 1 | 9 | 1:4 | UP | 12.5 | 25
234 | Mindray (P&B) | 1 | 9 | 1:4 | UP | 12.5 | 25
235 | Mindray (P&B) | 1 | 9 | 1:4 | UP | 12.5 | 25
236 | Mindray (P&B) | 1 | 9 | 1:4 | UP | 12.5 | 25
237 | Mindray (P&B) | 1 | 9 | 1:4 | UP | 12.5 | 25
238 | Mindray (P&B) | 1 | 9 | 1:4 | UP | 12.5 | 25
239 | Mindray (P&B) | 1 | 9 | 1:4 | UP | 12.5 | 25
240 | Mindray (P&B) | 1 | 9 | 1:4 | UP | 12.5 | 25
241 | Mindray (P&B) | 1 | 11 | 1:5 | DOWN | 12.5 | 25
242 | Mindray (P&B) | 1 | 11 | 1:5 | DOWN | 12.5 | 25
243 | Mindray (P&B) | 1 | 11 | 1:5 | DOWN | 12.5 | 25
244 | Mindray (P&B) | 1 | 11 | 1:5 | DOWN | 12.5 | 25
245 | Mindray (P&B) | 1 | 11 | 1:5 | DOWN | 12.5 | 25
246 | Mindray (P&B) | 1 | 11 | 1:5 | DOWN | 12.5 | 25
247 | Mindray (P&B) | 1 | 11 | 1:5 | DOWN | 12.5 | 25
248 | Mindray (P&B) | 1 | 11 | 1:5 | DOWN | 12.5 | 25
249 | Mindray (P&B) | 1 | 11 | 1:5 | DOWN | 12.5 | 25
250 | Mindray (P&B) | 1 | 11 | 1:5 | DOWN | 12.5 | 25
251 | Mindray (P&B) | 1 | 11 | 1:5 | DOWN | 12.5 | 25
252 | Mindray (P&B) | 1 | 11 | 1:5 | DOWN | 12.5 | 25
253 | Mindray (P&B) | 1 | 11 | 1:5 | DOWN | 12.5 | 25
254 | Mindray (P&B) | 1 | 11 | 1:5 | DOWN | 12.5 | 25
255 | Mindray (P&B) | 1 | 11 | 1:5 | DOWN | 12.5 | 25
256 | Mindray (P&B) | 1 | 11 | 1:5 | DOWN | 12.5 | 25
257 | Mindray (P&B) | 1 | 9 | 1:5 | UP | 12.5 | 25
258 | Mindray (P&B) | 1 | 9 | 1:5 | UP | 12.5 | 25
259 | Mindray (P&B) | 1 | 9 | 1:5 | UP | 12.5 | 25
260 | Mindray (P&B) | 1 | 9 | 1:5 | UP | 12.5 | 25
261 | Mindray (P&B) | 1 | 9 | 1:5 | UP | 12.5 | 25
262 | Mindray (P&B) | 1 | 9 | 1:5 | UP | 12.5 | 25
263 | Mindray (P&B) | 1 | 9 | 1:5 | UP | 12.5 | 25
264 | Mindray (P&B) | 1 | 9 | 1:5 | UP | 12.5 | 25
265 | Mindray (P&B) | 1 | 9 | 1:5 | UP | 12.5 | 25
266 | Mindray (P&B) | 1 | 9 | 1:5 | UP | 12.5 | 25
267 | Mindray (P&B) | 1 | 9 | 1:5 | UP | 12.5 | 25
268 | Mindray (P&B) | 1 | 9 | 1:5 | UP | 12.5 | 25
269 | Mindray (P&B) | 1 | 9 | 1:5 | UP | 12.5 | 25
270 | Mindray (P&B) | 1 | 9 | 1:5 | UP | 12.5 | 25
271 | Mindray (P&B) | 1 | 9 | 1:5 | UP | 12.5 | 25
272 | Mindray (P&B) | 1 | 9 | 1:5 | UP | 12.5 | 25
273 | Mindray (P&B) | 1 | 8 | 1:5 | DOWN | 12.5 | 25
274 | Mindray (P&B) | 1 | 8 | 1:5 | DOWN | 12.5 | 25
275 | Mindray (P&B) | 1 | 8 | 1:5 | DOWN | 12.5 | 25
276 | Mindray (P&B) | 1 | 8 | 1:5 | DOWN | 12.5 | 25
277 | Mindray (P&B) | 1 | 8 | 1:5 | DOWN | 12.5 | 25
278 | Mindray (P&B) | 1 | 8 | 1:5 | DOWN | 12.5 | 25
279 | Mindray (P&B) | 1 | 8 | 1:5 | DOWN | 12.5 | 25
280 | Mindray (P&B) | 1 | 8 | 1:5 | DOWN | 12.5 | 25
281 | Mindray (P&B) | 1 | 8 | 1:5 | DOWN | 12.5 | 25
282 | Mindray (P&B) | 1 | 8 | 1:5 | DOWN | 12.5 | 25
283 | Mindray (P&B) | 1 | 8 | 1:5 | DOWN | 12.5 | 25
284 | Mindray (P&B) | 1 | 8 | 1:5 | DOWN | 12.5 | 25
285 | Mindray (P&B) | 1 | 8 | 1:5 | DOWN | 12.5 | 25
286 | Mindray (P&B) | 1 | 8 | 1:5 | DOWN | 12.5 | 25
287 | Mindray (P&B) | 1 | 8 | 1:5 | DOWN | 12.5 | 25
288 | Mindray (P&B) | 1 | 8 | 1:5 | DOWN | 12.5 | 25
289 | Mindray (P&B) | 1 | 10 | 1:6 | UP | 12.5 | 25
290 | Mindray (P&B) | 1 | 10 | 1:6 | UP | 12.5 | 25
291 | Mindray (P&B) | 1 | 10 | 1:6 | UP | 12.5 | 25
292 | Mindray (P&B) | 1 | 10 | 1:6 | UP | 12.5 | 25
293 | Mindray (P&B) | 1 | 10 | 1:6 | UP | 12.5 | 25
294 | Mindray (P&B) | 1 | 10 | 1:6 | UP | 12.5 | 25
295 | Mindray (P&B) | 1 | 10 | 1:6 | UP | 12.5 | 25
296 | Mindray (P&B) | 1 | 10 | 1:6 | UP | 12.5 | 25
297 | Mindray (P&B) | 1 | 10 | 1:6 | UP | 12.5 | 25
298 | Mindray (P&B) | 1 | 10 | 1:6 | UP | 12.5 | 25
299 | Mindray (P&B) | 1 | 10 | 1:6 | UP | 12.5 | 25
300 | Mindray (P&B) | 1 | 10 | 1:6 | UP | 12.5 | 25
301 | Mindray (P&B) | 1 | 10 | 1:6 | UP | 12.5 | 25
302 | Mindray (P&B) | 1 | 10 | 1:6 | UP | 12.5 | 25
303 | Mindray (P&B) | 1 | 10 | 1:6 | UP | 12.5 | 25
304 | Mindray (P&B) | 1 | 10 | 1:6 | UP | 12.5 | 25
305 | Mindray (P&B) | 1 | 8 | 1:6 | DOWN | 12.5 | 25
306 | Mindray (P&B) | 1 | 8 | 1:6 | DOWN | 12.5 | 25
307 | Mindray (P&B) | 1 | 8 | 1:6 | DOWN | 12.5 | 25
308 | Mindray (P&B) | 1 | 8 | 1:6 | DOWN | 12.5 | 25
309 | Mindray (P&B) | 1 | 8 | 1:6 | DOWN | 12.5 | 25
310 | Mindray (P&B) | 1 | 8 | 1:6 | DOWN | 12.5 | 25
311 | Mindray (P&B) | 1 | 8 | 1:6 | DOWN | 12.5 | 25
312 | Mindray (P&B) | 1 | 8 | 1:6 | DOWN | 12.5 | 25
313 | Mindray (P&B) | 1 | 8 | 1:6 | DOWN | 12.5 | 25
314 | Mindray (P&B) | 1 | 8 | 1:6 | DOWN | 12.5 | 25
315 | Mindray (P&B) | 1 | 8 | 1:6 | DOWN | 12.5 | 25
316 | Mindray (P&B) | 1 | 8 | 1:6 | DOWN | 12.5 | 25
317 | Mindray (P&B) | 1 | 8 | 1:6 | DOWN | 12.5 | 25
318 | Mindray (P&B) | 1 | 8 | 1:6 | DOWN | 12.5 | 25
319 | Mindray (P&B) | 1 | 8 | 1:6 | DOWN | 12.5 | 25
320 | Mindray (P&B) | 1 | 8 | 1:6 | DOWN | 12.5 | 25
321 | Mindray (P&B) | 1 | 8 | 1:7 | UP | 12.5 | 25
322 | Mindray (P&B) | 1 | 8 | 1:7 | UP | 12.5 | 25
323 | Mindray (P&B) | 1 | 8 | 1:7 | UP | 12.5 | 25
324 | Mindray (P&B) | 1 | 8 | 1:7 | UP | 12.5 | 25
325 | Mindray (P&B) | 1 | 8 | 1:7 | UP | 12.5 | 25
326 | Mindray (P&B) | 1 | 8 | 1:7 | UP | 12.5 | 25
327 | Mindray (P&B) | 1 | 8 | 1:7 | UP | 12.5 | 25
328 | Mindray (P&B) | 1 | 8 | 1:7 | UP | 12.5 | 25
329 | Mindray (P&B) | 1 | 8 | 1:7 | UP | 12.5 | 25
330 | Mindray (P&B) | 1 | 8 | 1:7 | UP | 12.5 | 25
331 | Mindray (P&B) | 1 | 8 | 1:7 | UP | 12.5 | 25
332 | Mindray (P&B) | 1 | 8 | 1:7 | UP | 12.5 | 25
333 | Mindray (P&B) | 1 | 8 | 1:7 | UP | 12.5 | 25
334 | Mindray (P&B) | 1 | 8 | 1:7 | UP | 12.5 | 25
335 | Mindray (P&B) | 1 | 8 | 1:7 | UP | 12.5 | 25
336 | Mindray (P&B) | 1 | 8 | 1:7 | UP | 12.5 | 25
337 | Mindray (P&B) | 2 | 35 | 1:1 | DOWN | 12.5 | 25
338 | Mindray (P&B) | 2 | 35 | 1:1 | DOWN | 12.5 | 25
339 | Mindray (P&B) | 2 | 35 | 1:1 | DOWN | 12.5 | 25
340 | Mindray (P&B) | 2 | 35 | 1:1 | DOWN | 12.5 | 25
341 | Mindray (P&B) | 2 | 35 | 1:1 | DOWN | 12.5 | 25
342 | Mindray (P&B) | 2 | 35 | 1:1 | DOWN | 12.5 | 25
343 | Mindray (P&B) | 2 | 35 | 1:1 | DOWN | 12.5 | 25
344 | Mindray (P&B) | 2 | 35 | 1:1 | DOWN | 12.5 | 25
345 | Mindray (P&B) | 2 | 35 | 1:1 | DOWN | 12.5 | 25
346 | Mindray (P&B) | 2 | 35 | 1:1 | DOWN | 12.5 | 25
347 | Mindray (P&B) | 2 | 35 | 1:1 | DOWN | 12.5 | 25
348 | Mindray (P&B) | 2 | 35 | 1:1 | DOWN | 12.5 | 25
349 | Mindray (P&B) | 2 | 35 | 1:1 | DOWN | 12.5 | 25
350 | Mindray (P&B) | 2 | 35 | 1:1 | DOWN | 12.5 | 25
351 | Mindray (P&B) | 2 | 35 | 1:1 | DOWN | 12.5 | 25
352 | Mindray (P&B) | 2 | 35 | 1:1 | DOWN | 12.5 | 25
353 | Mindray (P&B) | 2 | 28 | 1:1 | UP | 12.5 | 25
354 | Mindray (P&B) | 2 | 28 | 1:1 | UP | 12.5 | 25
355 | Mindray (P&B) | 2 | 28 | 1:1 | UP | 12.5 | 25
356 | Mindray (P&B) | 2 | 28 | 1:1 | UP | 12.5 | 25
357 | Mindray (P&B) | 2 | 28 | 1:1 | UP | 12.5 | 25
358 | Mindray (P&B) | 2 | 28 | 1:1 | UP | 12.5 | 25
359 | Mindray (P&B) | 2 | 28 | 1:1 | UP | 12.5 | 25
360 | Mindray (P&B) | 2 | 28 | 1:1 | UP | 12.5 | 25
361 | Mindray (P&B) | 2 | 28 | 1:1 | UP | 12.5 | 25
362 | Mindray (P&B) | 2 | 28 | 1:1 | UP | 12.5 | 25
363 | Mindray (P&B) | 2 | 28 | 1:1 | UP | 12.5 | 25
364 | Mindray (P&B) | 2 | 28 | 1:1 | UP | 12.5 | 25
365 | Mindray (P&B) | 2 | 28 | 1:1 | UP | 12.5 | 25
366 | Mindray (P&B) | 2 | 28 | 1:1 | UP | 12.5 | 25
367 | Mindray (P&B) | 2 | 28 | 1:1 | UP | 12.5 | 25
368 | Mindray (P&B) | 2 | 28 | 1:1 | UP | 12.5 | 25
369 | Mindray (P&B) | 2 | 23 | 1:1 | DOWN | 12.5 | 25
370 | Mindray (P&B) | 2 | 23 | 1:1 | DOWN | 12.5 | 25
371 | Mindray (P&B) | 2 | 23 | 1:1 | DOWN | 12.5 | 25
372 | Mindray (P&B) | 2 | 23 | 1:1 | DOWN | 12.5 | 25
373 | Mindray (P&B) | 2 | 23 | 1:1 | DOWN | 12.5 | 25
374 | Mindray (P&B) | 2 | 23 | 1:1 | DOWN | 12.5 | 25
375 | Mindray (P&B) | 2 | 23 | 1:1 | DOWN | 12.5 | 25
376 | Mindray (P&B) | 2 | 23 | 1:1 | DOWN | 12.5 | 25
377 | Mindray (P&B) | 2 | 23 | 1:1 | DOWN | 12.5 | 25
378 | Mindray (P&B) | 2 | 23 | 1:1 | DOWN | 12.5 | 25
379 | Mindray (P&B) | 2 | 23 | 1:1 | DOWN | 12.5 | 25
380 | Mindray (P&B) | 2 | 23 | 1:1 | DOWN | 12.5 | 25
381 | Mindray (P&B) | 2 | 23 | 1:1 | DOWN | 12.5 | 25
382 | Mindray (P&B) | 2 | 23 | 1:1 | DOWN | 12.5 | 25
383 | Mindray (P&B) | 2 | 23 | 1:1 | DOWN | 12.5 | 25
384 | Mindray (P&B) | 2 | 23 | 1:1 | DOWN | 12.5 | 25
385 | Mindray (P&B) | 2 | 23 | 1:2 | UP | 12.5 | 25
386 | Mindray (P&B) | 2 | 23 | 1:2 | UP | 12.5 | 25
387 | Mindray (P&B) | 2 | 23 | 1:2 | UP | 12.5 | 25
388 | Mindray (P&B) | 2 | 23 | 1:2 | UP | 12.5 | 25
389 | Mindray (P&B) | 2 | 23 | 1:2 | UP | 12.5 | 25
390 | Mindray (P&B) | 2 | 23 | 1:2 | UP | 12.5 | 25
391 | Mindray (P&B) | 2 | 23 | 1:2 | UP | 12.5 | 25
392 | Mindray (P&B) | 2 | 23 | 1:2 | UP | 12.5 | 25
393 | Mindray (P&B) | 2 | 23 | 1:2 | UP | 12.5 | 25
394 | Mindray (P&B) | 2 | 23 | 1:2 | UP | 12.5 | 25
395 | Mindray (P&B) | 2 | 23 | 1:2 | UP | 12.5 | 25
396 | Mindray (P&B) | 2 | 23 | 1:2 | UP | 12.5 | 25
397 | Mindray (P&B) | 2 | 23 | 1:2 | UP | 12.5 | 25
398 | Mindray (P&B) | 2 | 23 | 1:2 | UP | 12.5 | 25
399 | Mindray (P&B) | 2 | 23 | 1:2 | UP | 12.5 | 25
400 | Mindray (P&B) | 2 | 23 | 1:2 | UP | 12.5 | 25
401 | Mindray (P&B) | 2 | 19 | 1:2 | DOWN | 12.5 | 25
402 | Mindray (P&B) | 2 | 19 | 1:2 | DOWN | 12.5 | 25
403 | Mindray (P&B) | 2 | 19 | 1:2 | DOWN | 12.5 | 25
404 | Mindray (P&B) | 2 | 19 | 1:2 | DOWN | 12.5 | 25
405 | Mindray (P&B) | 2 | 19 | 1:2 | DOWN | 12.5 | 25
406 | Mindray (P&B) | 2 | 19 | 1:2 | DOWN | 12.5 | 25
407 | Mindray (P&B) | 2 | 19 | 1:2 | DOWN | 12.5 | 25
408 | Mindray (P&B) | 2 | 19 | 1:2 | DOWN | 12.5 | 25
409 | Mindray (P&B) | 2 | 19 | 1:2 | DOWN | 12.5 | 25
410 | Mindray (P&B) | 2 | 19 | 1:2 | DOWN | 12.5 | 25
411 | Mindray (P&B) | 2 | 19 | 1:2 | DOWN | 12.5 | 25
412 | Mindray (P&B) | 2 | 19 | 1:2 | DOWN | 12.5 | 25
413 | Mindray (P&B) | 2 | 19 | 1:2 | DOWN | 12.5 | 25
414 | Mindray (P&B) | 2 | 19 | 1:2 | DOWN | 12.5 | 25
415 | Mindray (P&B) | 2 | 19 | 1:2 | DOWN | 12.5 | 25
416 | Mindray (P&B) | 2 | 19 | 1:2 | DOWN | 12.5 | 25
417 | Mindray (P&B) | 2 | 15 | 1:2 | UP | 12.5 | 25
418 | Mindray (P&B) | 2 | 15 | 1:2 | UP | 12.5 | 25
419 | Mindray (P&B) | 2 | 15 | 1:2 | UP | 12.5 | 25
420 | Mindray (P&B) | 2 | 15 | 1:2 | UP | 12.5 | 25
421 | Mindray (P&B) | 2 | 15 | 1:2 | UP | 12.5 | 25
422 | Mindray (P&B) | 2 | 15 | 1:2 | UP | 12.5 | 25
423 | Mindray (P&B) | 2 | 15 | 1:2 | UP | 12.5 | 25
424 | Mindray (P&B) | 2 | 15 | 1:2 | UP | 12.5 | 25
425 | Mindray (P&B) | 2 | 15 | 1:2 | UP | 12.5 | 25
426 | Mindray (P&B) | 2 | 15 | 1:2 | UP | 12.5 | 25
427 | Mindray (P&B) | 2 | 15 | 1:2 | UP | 12.5 | 25
428 | Mindray (P&B) | 2 | 15 | 1:2 | UP | 12.5 | 25
429 | Mindray (P&B) | 2 | 15 | 1:2 | UP | 12.5 | 25
430 | Mindray (P&B) | 2 | 15 | 1:2 | UP | 12.5 | 25
431 | Mindray (P&B) | 2 | 15 | 1:2 | UP | 12.5 | 25
432 | Mindray (P&B) | 2 | 15 | 1:2 | UP | 12.5 | 25
433 | Mindray (P&B) | 2 | 17 | 1:3 | DOWN | 12.5 | 25
434 | Mindray (P&B) | 2 | 17 | 1:3 | DOWN | 12.5 | 25
435 | Mindray (P&B) | 2 | 17 | 1:3 | DOWN | 12.5 | 25
436 | Mindray (P&B) | 2 | 17 | 1:3 | DOWN | 12.5 | 25
437 | Mindray (P&B) | 2 | 17 | 1:3 | DOWN | 12.5 | 25
438 | Mindray (P&B) | 2 | 17 | 1:3 | DOWN | 12.5 | 25
439 | Mindray (P&B) | 2 | 17 | 1:3 | DOWN | 12.5 | 25
440 | Mindray (P&B) | 2 | 17 | 1:3 | DOWN | 12.5 | 25
441 | Mindray (P&B) | 2 | 17 | 1:3 | DOWN | 12.5 | 25
442 | Mindray (P&B) | 2 | 17 | 1:3 | DOWN | 12.5 | 25
443 | Mindray (P&B) | 2 | 17 | 1:3 | DOWN | 12.5 | 25
444 | Mindray (P&B) | 2 | 17 | 1:3 | DOWN | 12.5 | 25
445 | Mindray (P&B) | 2 | 17 | 1:3 | DOWN | 12.5 | 25
446 | Mindray (P&B) | 2 | 17 | 1:3 | DOWN | 12.5 | 25
447 | Mindray (P&B) | 2 | 17 | 1:3 | DOWN | 12.5 | 25
448 | Mindray (P&B) | 2 | 17 | 1:3 | DOWN | 12.5 | 25
449 | Mindray (P&B) | 2 | 14 | 1:3 | UP | 12.5 | 25
450 | Mindray (P&B) | 2 | 14 | 1:3 | UP | 12.5 | 25
451 | Mindray (P&B) | 2 | 14 | 1:3 | UP | 12.5 | 25
452 | Mindray (P&B) | 2 | 14 | 1:3 | UP | 12.5 | 25
453 | Mindray (P&B) | 2 | 14 | 1:3 | UP | 12.5 | 25
454 | Mindray (P&B) | 2 | 14 | 1:3 | UP | 12.5 | 25
455 | Mindray (P&B) | 2 | 14 | 1:3 | UP | 12.5 | 25
456 | Mindray (P&B) | 2 | 14 | 1:3 | UP | 12.5 | 25
457 | Mindray (P&B) | 2 | 14 | 1:3 | UP | 12.5 | 25
458 | Mindray (P&B) | 2 | 14 | 1:3 | UP | 12.5 | 25
459 | Mindray (P&B) | 2 | 14 | 1:3 | UP | 12.5 | 25
460 | Mindray (P&B) | 2 | 14 | 1:3 | UP | 12.5 | 25
461 | Mindray (P&B) | 2 | 14 | 1:3 | UP | 12.5 | 25
462 | Mindray (P&B) | 2 | 14 | 1:3 | UP | 12.5 | 25
463 | Mindray (P&B) | 2 | 14 | 1:3 | UP | 12.5 | 25
464 | Mindray (P&B) | 2 | 14 | 1:3 | UP | 12.5 | 25
465 | Mindray (P&B) | 2 | 12 | 1:3 | DOWN | 12.5 | 25
466 | Mindray (P&B) | 2 | 12 | 1:3 | DOWN | 12.5 | 25
467 | Mindray (P&B) | 2 | 12 | 1:3 | DOWN | 12.5 | 25
468 | Mindray (P&B) | 2 | 12 | 1:3 | DOWN | 12.5 | 25
469 | Mindray (P&B) | 2 | 12 | 1:3 | DOWN | 12.5 | 25
470 | Mindray (P&B) | 2 | 12 | 1:3 | DOWN | 12.5 | 25
471 | Mindray (P&B) | 2 | 12 | 1:3 | DOWN | 12.5 | 25
472 | Mindray (P&B) | 2 | 12 | 1:3 | DOWN | 12.5 | 25
473 | Mindray (P&B) | 2 | 12 | 1:3 | DOWN | 12.5 | 25
474 | Mindray (P&B) | 2 | 12 | 1:3 | DOWN | 12.5 | 25
475 | Mindray (P&B) | 2 | 12 | 1:3 | DOWN | 12.5 | 25
476 | Mindray (P&B) | 2 | 12 | 1:3 | DOWN | 12.5 | 25
477 | Mindray (P&B) | 2 | 12 | 1:3 | DOWN | 12.5 | 25
478 | Mindray (P&B) | 2 | 12 | 1:3 | DOWN | 12.5 | 25
479 | Mindray (P&B) | 2 | 12 | 1:3 | DOWN | 12.5 | 25
480 | Mindray (P&B) | 2 | 12 | 1:3 | DOWN | 12.5 | 25
481 | Mindray (P&B) | 2 | 14 | 1:4 | UP | 12.5 | 25
482 | Mindray (P&B) | 2 | 14 | 1:4 | UP | 12.5 | 25
483 | Mindray (P&B) | 2 | 14 | 1:4 | UP | 12.5 | 25
484 | Mindray (P&B) | 2 | 14 | 1:4 | UP | 12.5 | 25
485 | Mindray (P&B) | 2 | 14 | 1:4 | UP | 12.5 | 25
486 | Mindray (P&B) | 2 | 14 | 1:4 | UP | 12.5 | 25
487 | Mindray (P&B) | 2 | 14 | 1:4 | UP | 12.5 | 25
488 | Mindray (P&B) | 2 | 14 | 1:4 | UP | 12.5 | 25
489 | Mindray (P&B) | 2 | 14 | 1:4 | UP | 12.5 | 25
490 | Mindray (P&B) | 2 | 14 | 1:4 | UP | 12.5 | 25
491 | Mindray (P&B) | 2 | 14 | 1:4 | UP | 12.5 | 25
492 | Mindray (P&B) | 2 | 14 | 1:4 | UP | 12.5 | 25
493 | Mindray (P&B) | 2 | 14 | 1:4 | UP | 12.5 | 25
494 | Mindray (P&B) | 2 | 14 | 1:4 | UP | 12.5 | 25
495 | Mindray (P&B) | 2 | 14 | 1:4 | UP | 12.5 | 25
496 | Mindray (P&B) | 2 | 14 | 1:4 | UP | 12.5 | 25
497 | Mindray (P&B) | 2 | 11 | 1:4 | DOWN | 12.5 | 25
498 | Mindray (P&B) | 2 | 11 | 1:4 | DOWN | 12.5 | 25
499 | Mindray (P&B) | 2 | 11 | 1:4 | DOWN | 12.5 | 25
500 | Mindray (P&B) | 2 | 11 | 1:4 | DOWN | 12.5 | 25
501 | Mindray (P&B) | 2 | 11 | 1:4 | DOWN | 12.5 | 25
502 | Mindray (P&B) | 2 | 11 | 1:4 | DOWN | 12.5 | 25
503 | Mindray (P&B) | 2 | 11 | 1:4 | DOWN | 12.5 | 25
504 | Mindray (P&B) | 2 | 11 | 1:4 | DOWN | 12.5 | 25
505 | Mindray (P&B) | 2 | 11 | 1:4 | DOWN | 12.5 | 25
506 | Mindray (P&B) | 2 | 11 | 1:4 | DOWN | 12.5 | 25
507 | Mindray (P&B) | 2 | 11 | 1:4 | DOWN | 12.5 | 25
508 | Mindray (P&B) | 2 | 11 | 1:4 | DOWN | 12.5 | 25
509 | Mindray (P&B) | 2 | 11 | 1:4 | DOWN | 12.5 | 25
510 | Mindray (P&B) | 2 | 11 | 1:4 | DOWN | 12.5 | 25
511 | Mindray (P&B) | 2 | 11 | 1:4 | DOWN | 12.5 | 25
512 | Mindray (P&B) | 2 | 11 | 1:4 | DOWN | 12.5 | 25
513 | Mindray (P&B) | 2 | 9 | 1:4 | UP | 12.5 | 25
514 | Mindray (P&B) | 2 | 9 | 1:4 | UP | 12.5 | 25
515 | Mindray (P&B) | 2 | 9 | 1:4 | UP | 12.5 | 25
516 | Mindray (P&B) | 2 | 9 | 1:4 | UP | 12.5 | 25
517 | Mindray (P&B) | 2 | 9 | 1:4 | UP | 12.5 | 25
518 | Mindray (P&B) | 2 | 9 | 1:4 | UP | 12.5 | 25
519 | Mindray (P&B) | 2 | 9 | 1:4 | UP | 12.5 | 25
520 | Mindray (P&B) | 2 | 9 | 1:4 | UP | 12.5 | 25
521 | Mindray (P&B) | 2 | 9 | 1:4 | UP | 12.5 | 25
522 | Mindray (P&B) | 2 | 9 | 1:4 | UP | 12.5 | 25
523 | Mindray (P&B) | 2 | 9 | 1:4 | UP | 12.5 | 25
524 | Mindray (P&B) | 2 | 9 | 1:4 | UP | 12.5 | 25
525 | Mindray (P&B) | 2 | 9 | 1:4 | UP | 12.5 | 25
526 | Mindray (P&B) | 2 | 9 | 1:4 | UP | 12.5 | 25
527 | Mindray (P&B) | 2 | 9 | 1:4 | UP | 12.5 | 25
528 | Mindray (P&B) | 2 | 9 | 1:4 | UP | 12.5 | 25
529 | Mindray (P&B) | 2 | 11 | 1:5 | DOWN | 12.5 | 25
530 | Mindray (P&B) | 2 | 11 | 1:5 | DOWN | 12.5 | 25
531 | Mindray (P&B) | 2 | 11 | 1:5 | DOWN | 12.5 | 25
532 | Mindray (P&B) | 2 | 11 | 1:5 | DOWN | 12.5 | 25
533 | Mindray (P&B) | 2 | 11 | 1:5 | DOWN | 12.5 | 25
534 | Mindray (P&B) | 2 | 11 | 1:5 | DOWN | 12.5 | 25
535 | Mindray (P&B) | 2 | 11 | 1:5 | DOWN | 12.5 | 25
536 | Mindray (P&B) | 2 | 11 | 1:5 | DOWN | 12.5 | 25
537 | Mindray (P&B) | 2 | 11 | 1:5 | DOWN | 12.5 | 25
538 | Mindray (P&B) | 2 | 11 | 1:5 | DOWN | 12.5 | 25
539 | Mindray (P&B) | 2 | 11 | 1:5 | DOWN | 12.5 | 25
540 | Mindray (P&B) | 2 | 11 | 1:5 | DOWN | 12.5 | 25
541 | Mindray (P&B) | 2 | 11 | 1:5 | DOWN | 12.5 | 25
542 | Mindray (P&B) | 2 | 11 | 1:5 | DOWN | 12.5 | 25
543 | Mindray (P&B) | 2 | 11 | 1:5 | DOWN | 12.5 | 25
544 | Mindray (P&B) | 2 | 11 | 1:5 | DOWN | 12.5 | 25
545 | Mindray (P&B) | 2 | 9 | 1:5 | UP | 12.5 | 25
546 | Mindray (P&B) | 2 | 9 | 1:5 | UP | 12.5 | 25
547 | Mindray (P&B) | 2 | 9 | 1:5 | UP | 12.5 | 25
548 | Mindray (P&B) | 2 | 9 | 1:5 | UP | 12.5 | 25
549 | Mindray (P&B) | 2 | 9 | 1:5 | UP | 12.5 | 25
550 | Mindray (P&B) | 2 | 9 | 1:5 | UP | 12.5 | 25
551 | Mindray (P&B) | 2 | 9 | 1:5 | UP | 12.5 | 25
552 | Mindray (P&B) | 2 | 9 | 1:5 | UP | 12.5 | 25
553 | Mindray (P&B) | 2 | 9 | 1:5 | UP | 12.5 | 25
554 | Mindray (P&B) | 2 | 9 | 1:5 | UP | 12.5 | 25
555 | Mindray (P&B) | 2 | 9 | 1:5 | UP | 12.5 | 25
556 | Mindray (P&B) | 2 | 9 | 1:5 | UP | 12.5 | 25
557 | Mindray (P&B) | 2 | 9 | 1:5 | UP | 12.5 | 25
558 | Mindray (P&B) | 2 | 9 | 1:5 | UP | 12.5 | 25
559 | Mindray (P&B) | 2 | 9 | 1:5 | UP | 12.5 | 25
560 | Mindray (P&B) | 2 | 9 | 1:5 | UP | 12.5 | 25
561 | Mindray (P&B) | 2 | 8 | 1:5 | DOWN | 12.5 | 25
562 | Mindray (P&B) | 2 | 8 | 1:5 | DOWN | 12.5 | 25
563 | Mindray (P&B) | 2 | 8 | 1:5 | DOWN | 12.5 | 25
564 | Mindray (P&B) | 2 | 8 | 1:5 | DOWN | 12.5 | 25
565 | Mindray (P&B) | 2 | 8 | 1:5 | DOWN | 12.5 | 25
566 | Mindray (P&B) | 2 | 8 | 1:5 | DOWN | 12.5 | 25
567 | Mindray (P&B) | 2 | 8 | 1:5 | DOWN | 12.5 | 25
568 | Mindray (P&B) | 2 | 8 | 1:5 | DOWN | 12.5 | 25
569 | Mindray (P&B) | 2 | 8 | 1:5 | DOWN | 12.5 | 25
570 | Mindray (P&B) | 2 | 8 | 1:5 | DOWN | 12.5 | 25
571 | Mindray (P&B) | 2 | 8 | 1:5 | DOWN | 12.5 | 25
572 | Mindray (P&B) | 2 | 8 | 1:5 | DOWN | 12.5 | 25
573 | Mindray (P&B) | 2 | 8 | 1:5 | DOWN | 12.5 | 25
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

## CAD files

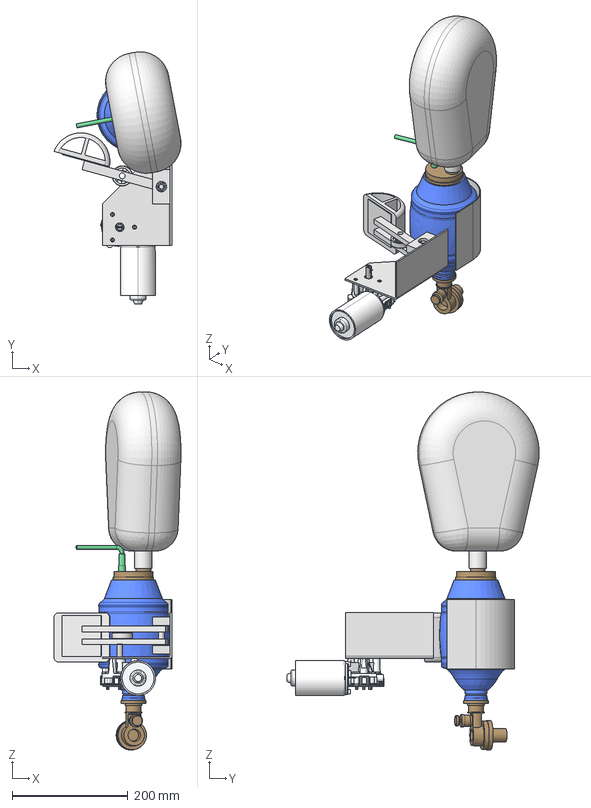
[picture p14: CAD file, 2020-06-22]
Arquivos CAD/Respirador V3.stp
219.3 x 435.7 x 618.3 mm
base
F006WMO310
%3% BS 290 - SKF 608 x 2
Mancal x 2
eixo
Haste x 2
%3% BS 290 - SKF 6300
chapa
suporte ambu
Corpo do Ambu
Tampa de Entrada
Bolsa de Carregamento
Adaptador de Saida
Corpo Valvula de Saida
Bocal de Saída
Corpo Valvula Reguladora de Pressão
Pino de Liberação Valvula Alivio de Pressã o
Tubo de Entrada do Ar
contato

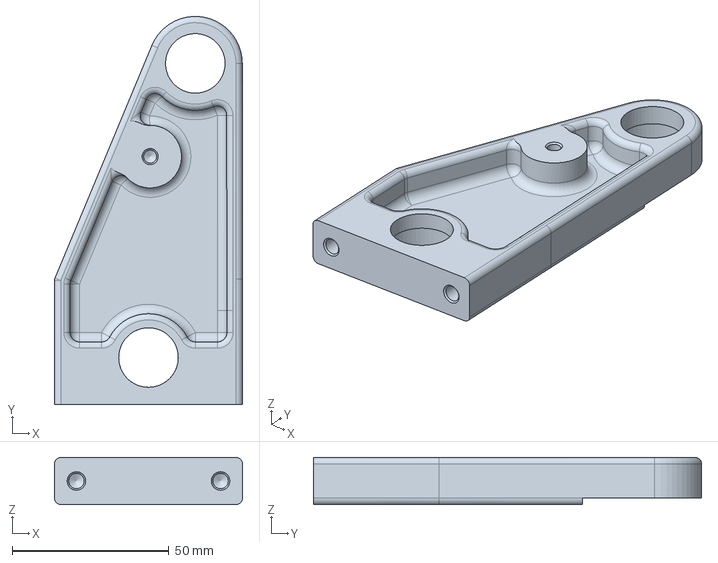
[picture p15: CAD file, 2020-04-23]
R3/Gcode/Suporte Direito (1).stp
60.0 x 123.9 x 15.0 mm

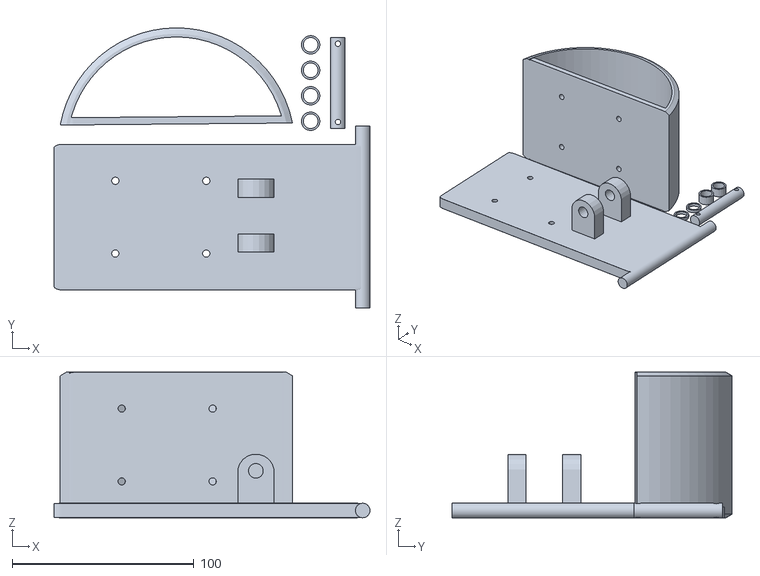
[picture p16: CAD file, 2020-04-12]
R3/Respirator_COVID19_Concept/files/Arm_R2_Respirator_COVID19_Concept.stl
173.7 x 154.0 x 80.0

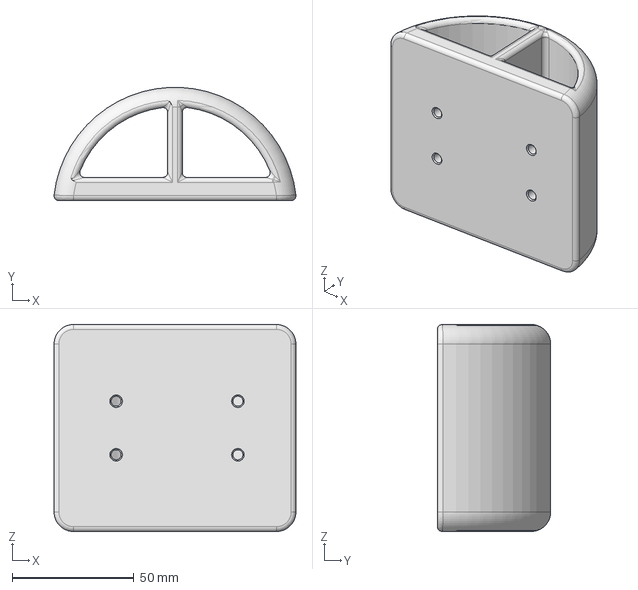
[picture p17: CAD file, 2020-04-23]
R3/Gcode/Apalpador do Ambu (1).stp
99.4 x 46.4 x 85.0 mm

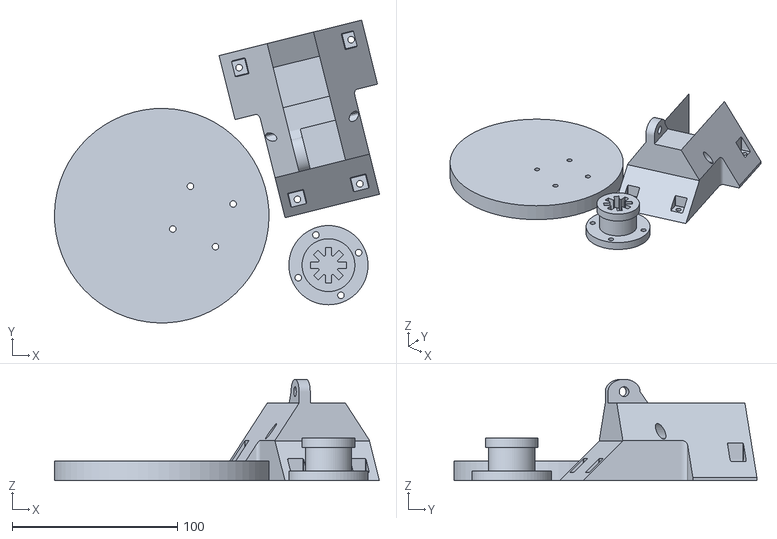
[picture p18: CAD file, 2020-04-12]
R3/Respirator_COVID19_Concept/files/Gear_R2_Respirator_COVID19_Concept.stl
196.9 x 183.5 x 61.5

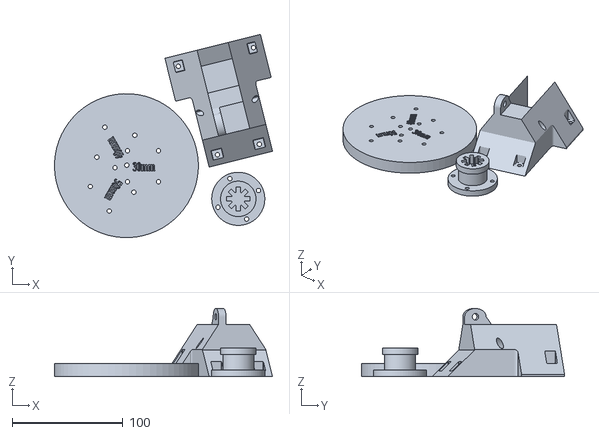
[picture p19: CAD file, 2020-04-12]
R3/Respirator_COVID19_Concept/files/Adjustable_Gear_R2_Respirator_COVID19_Concept.stl
196.9 x 183.5 x 61.5

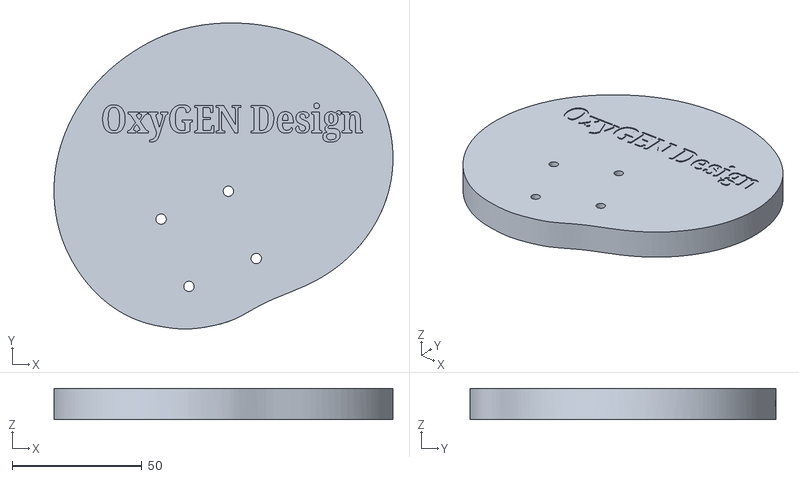
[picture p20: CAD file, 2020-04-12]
R3/Respirator_COVID19_Concept/files/Alternative_Gear_R3_Respirator_COVID19_Concept.stl
130.4 x 117.7 x 12.0

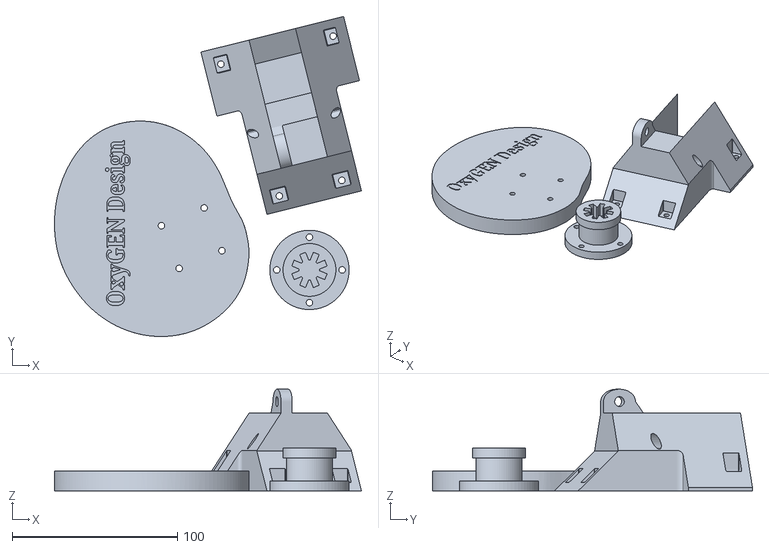
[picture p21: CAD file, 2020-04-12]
R3/Respirator_COVID19_Concept/files/Gear_R3_Respirator_COVID19_Concept.stl
185.8 x 193.7 x 61.5

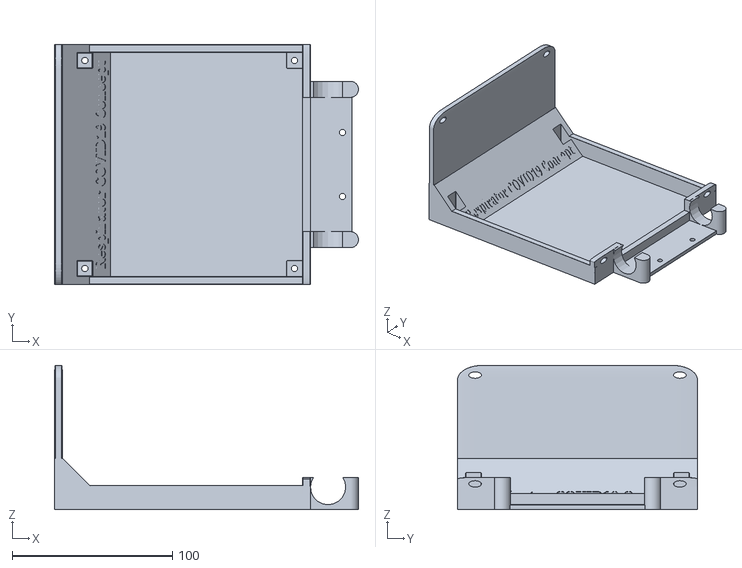
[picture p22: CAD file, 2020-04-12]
R3/Respirator_COVID19_Concept/files/Base_R2_Respirator_COVID19_Concept.stl
190.0 x 150.0 x 90.0

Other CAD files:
desenhos/Desenhos_DWG/Desenho n.07_fl1_Folha_1.dwg
desenhos/Desenhos_DWG/Desenho n.07_fl1_Folha_2.dwg
desenhos/Desenhos_DWG/#Desenho n.05_fl1_Folha_1.dwg
R3/Gcode/Suporte Esquerdo (1).stp
desenhos/Desenhos_DWG/Desenho n.05_fl1_Folha_2.dwg
Arquivos CAD/Adaptador de Saida.ipt
Arquivos CAD/Bocal de Saída.ipt
Arquivos CAD/Bolsa de Carregamento.ipt
Arquivos CAD/Conjunto Ambu.iam
Arquivos CAD/Corpo Valvula Reguladora de Pressão.ipt
Arquivos CAD/Corpo Valvula de Saida.ipt
Arquivos CAD/Corpo do Ambu.ipt
Arquivos CAD/F006WMO310.ipt
Arquivos CAD/Haste.ipt
Arquivos CAD/Pino de Liberação Valvula Alivio de Pressão.ipt
Arquivos CAD/Respirador V3.iam
Arquivos CAD/Tampa de Entrada.ipt
Arquivos CAD/Tubo de Entrada do Ar.ipt
Arquivos CAD/base.ipt
Arquivos CAD/chapa.ipt
Arquivos CAD/contato.ipt
Arquivos CAD/eixo.ipt
Arquivos CAD/suporte ambu.ipt
desenhos/Desenhos_DWG/Desenho n.05_fl1_Folha_1.dwg

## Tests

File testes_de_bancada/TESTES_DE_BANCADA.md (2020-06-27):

# Descrição dos Testes Funcionais de Bancada (in vitro)

## 1) Levantamento preliminar da Relação PEEP x Pressão Expiratória Máxima (Vál. VAP) x Freq. Respiratória x Volume Inspirado

### Descrição da Fig. 1: 
*Eixo x:* representa a leitura da pressão máxima no final da inspiração medida com o equipamento padrão ouro (Fluke).

*Eixo y :* apresenta a pressão regulada na válvula VAP (azul) ou a pressão medida no sensor de pressão do AraPlus (laranja).

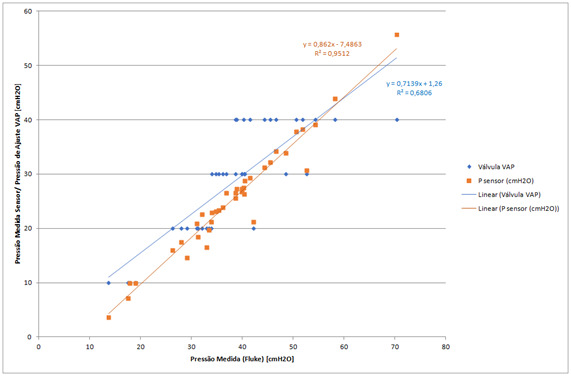
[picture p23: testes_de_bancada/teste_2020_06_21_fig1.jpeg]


### Conclusões

1.1 - A pressão da válvula VAP apresenta uma grande dispersão da pressão de atuação

1.2 - Sensor de pressão do AraPlus apresenta uma boa correlação e linearidade com o sensor padrão ouro.

1.3 - Equação de ajuste do sensor de pressão do AraPlus precisa ser revista, pois a calibração estática feita anteriormente não está batendo com as medições feitas com o padrão ouro. 

1.4 - Dǘvida: Deveríamos fazer a calibração pelo valor do pico da pressão, medida dinamicamente ou adquirir um manômetro profissional para fazer a calibração estática, uma vez que a calibração foi feita com uma manômetro em U caseiro?

1.5 - Será necessário estabelecer procedimento de calibração (analógica e/ou digital)

### Descrição da Fig. 2:

*Eixo x*: representa a leitura da pressão máxima no final da inspiração medida com o equipamento padrão ouro (Fluke).

*Eixo y* : apresenta a pressão que foi ajustada manualmente nas válvulas VAP e PEEP em quatro condições: apenas a VAP (roxo), apenas a PEEP (cinza), VAP+PEEP (laranja) VAP-PEEP (azul)

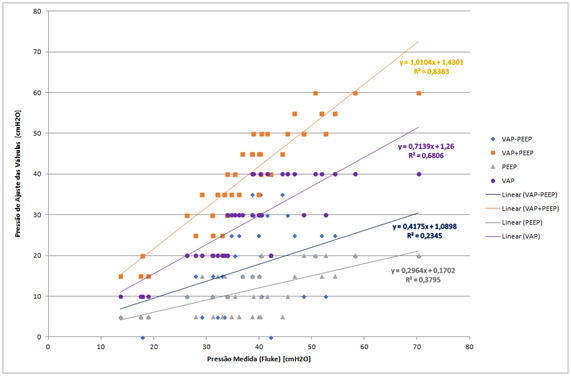
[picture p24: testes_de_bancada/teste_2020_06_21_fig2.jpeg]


### Conclusões

2.1 - Setup da PEEP impacta na pressão máxima.

2.2 - Pressão máxima no final da inspiração tem alta correlação com a soma das pressões ajustadas manualmente PEEP+VAP, pois o coeficiente angular a curva laranja é próximo de 1. 

2.3 - A conclusão anterior leva a crer que ao regular a pressão na válvula VAP, o invés dela limitar a presão máxima ao final de inspiração, ela está funcionando como uma regulagem da Driving Pressure (DP), que é o delta de pressão que se coloca sobre a PEEP durante a inspiração (Pmax = DP + PEEP). 

### Descrição da Fig. 3:

*Eixo x:* representa a pressão que foi ajustada manualmente na válvula VAP 

*Eixo y:* representa a pressão de leitura do sensor padrão ouro (Fluke)

Este gráfico é plotagem dos dados mostrados na curva azul da Fig.1, porém discretizados para diferente valores de ajuste da válvula PEEP

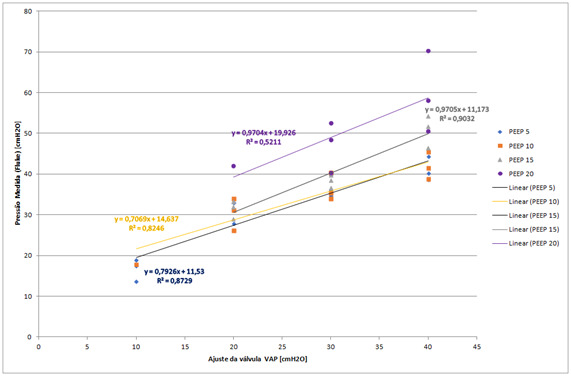
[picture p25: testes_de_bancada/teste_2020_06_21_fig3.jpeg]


### Conclusões
3.1 – Hipótese: a pressão máxima (VAP) deve ser ajustada em função de curvas para cada valor de PEEP ajustado.

### Descrição da Fig. 4:

*Eixo x:*  representa a diferença entre os dois valores ajustadoa manualmente entre VAP e PEEP

*Eixo y:* volume inspirado com o sensor padrão ouro (fluke)

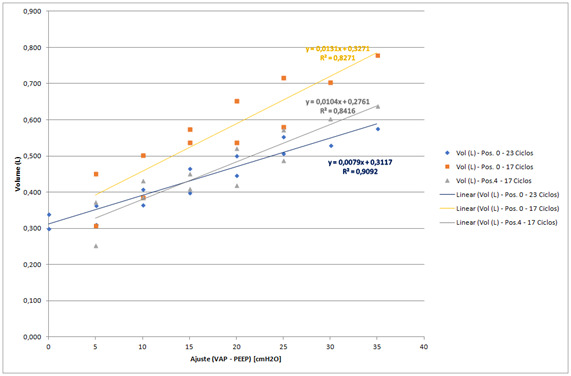
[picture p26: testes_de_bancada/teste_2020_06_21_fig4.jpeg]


### Conclusões
4.1 - Existe uma correlação razoável entre o volume e a diferença de pressão (VAP-PEEP).

4.2 - Dúvida: qual seria o significado da diferença VAP-PEEP?

4.3 - Hipótese: Para uma determinada complacência, o volume varia proporcionalmente com a posição do AMBU para qualquer ajuste das válvulas.

4.4 - Hipótese: Para uma determinada complacência, o volume por ciclo não varia proporcionalmente com o tempo de inspiração.

4.5 - Dúvida: valeria a pena continuar correlacionando as pressões de ajuste das válvulas VAP e PEEP com o volume inspirado uma vez que o AraPlus não mede volume e a complacência do pulmão varia de paciente para paciente?

## 2) Levantamento da freqüência de operação, e relações Ti:Te possíveis

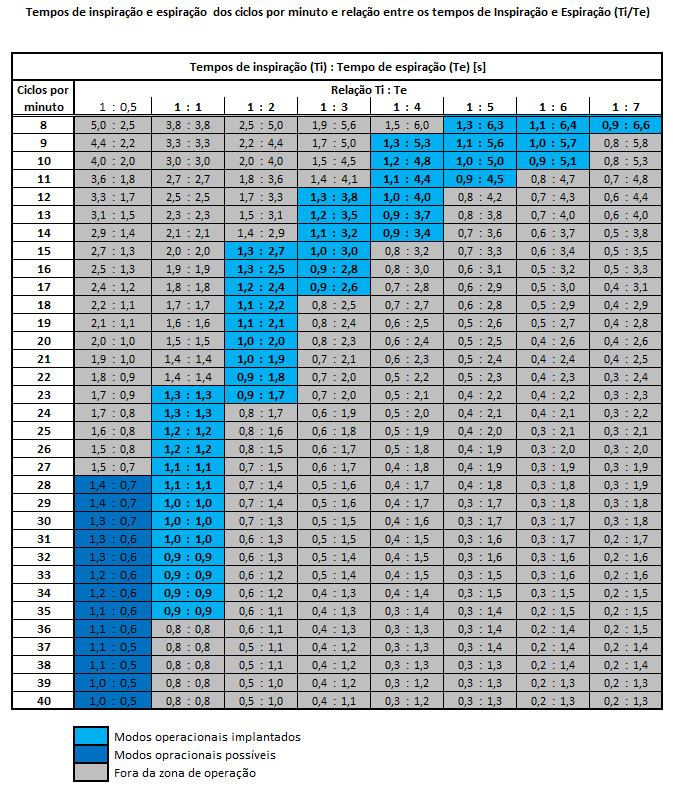
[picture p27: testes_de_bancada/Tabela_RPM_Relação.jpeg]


As freqüências e tempos foram levantada com base nos sensores instalados no acionamento mecânico.

## 3) Levantamento da relação de tempos determinadas mecanicamente e pelas curvas de pressão pneumática

Averiguar para diversas condições se os tempos Ti e Te medidos pelos sensores posicionados no eixo do motor corresponde aos tempos de Ti e Te medidos pela curva de pressão/ fluxo pneumático.

## 4) Levantamento da Relação de FIO2 e Fluxo de Oxigênio (Fluxímetro de parede)

Referência: GODOY, Armando Carlos Franco de; VIEIRA, Ronan José. Comparação da FiO2 fornecida por sete modelos de sistema balão-máscara auto-inflável. Rev. Bras. Anestesiol., Campinas , v. 59, n. 1, p. 21-27, Feb. 2009 . Available from <http://www.scielo.br/scielo.php?script=sci_arttext&pid=S0034-70942009000100004&lng=en&nrm=iso>. access on 22 June 2020. https://doi.org/10.1590/S0034-70942009000100004.

## 5) Calibração Estática do Sensor de Pressão

### Descrição

Levantar curva de pressão medida pelo sensor MPX5500DP comparando com uma medição de pressão estática (com manômetro U ou manômetro analógico)

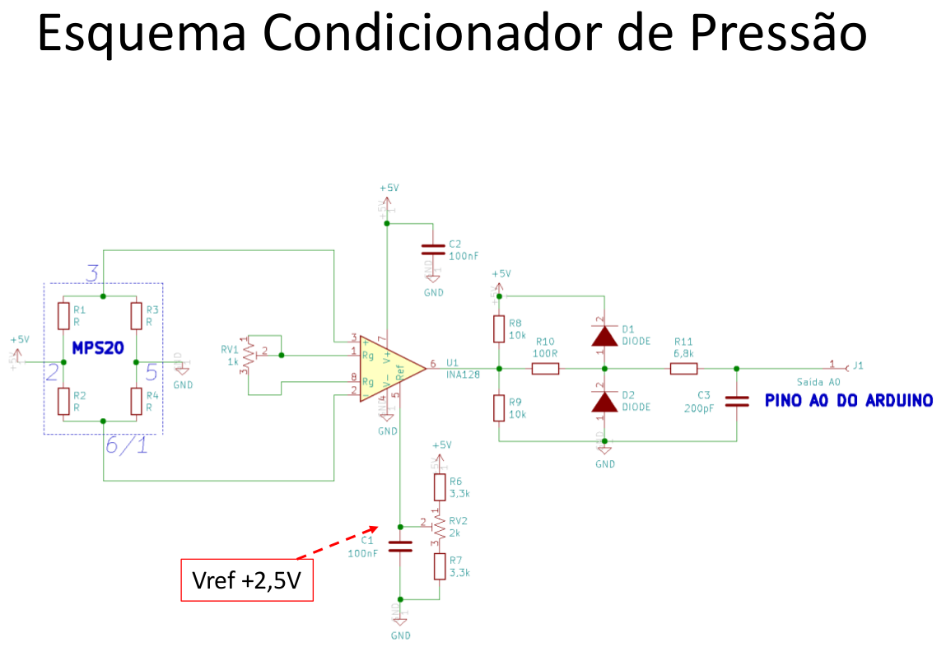
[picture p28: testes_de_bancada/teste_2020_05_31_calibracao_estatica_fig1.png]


Diagrama elétrico do circuito de condicionamento de pressão utilizado no AraPlus

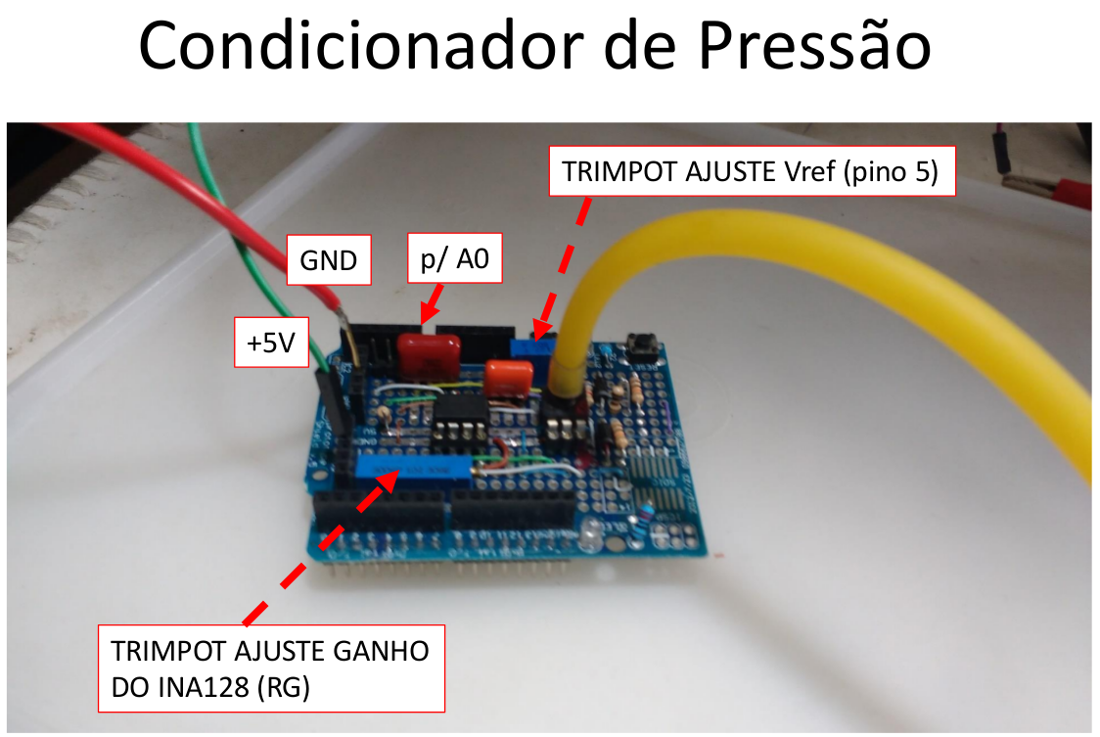
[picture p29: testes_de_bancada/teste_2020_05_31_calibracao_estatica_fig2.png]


Implementação do circuito de condicionamento 

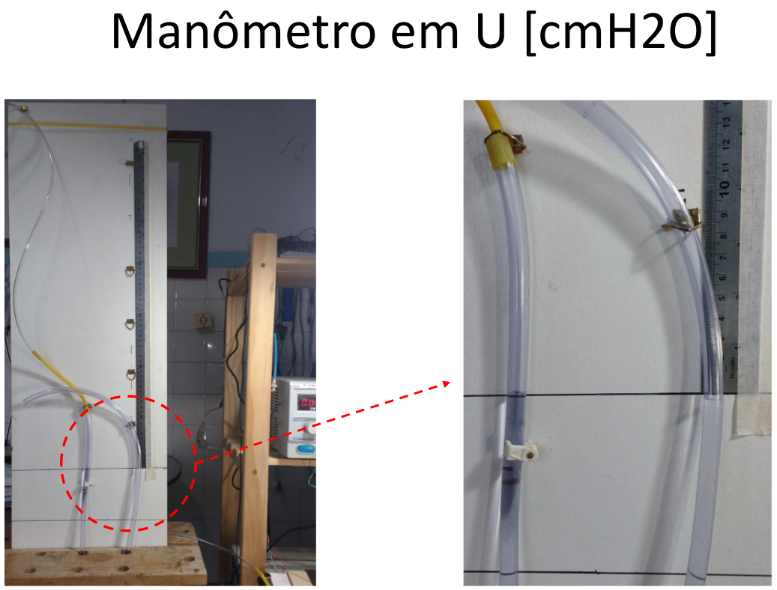
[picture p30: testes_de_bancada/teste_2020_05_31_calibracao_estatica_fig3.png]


Foto do manômetro em U caseiro utilizado na calibração

### Resultados

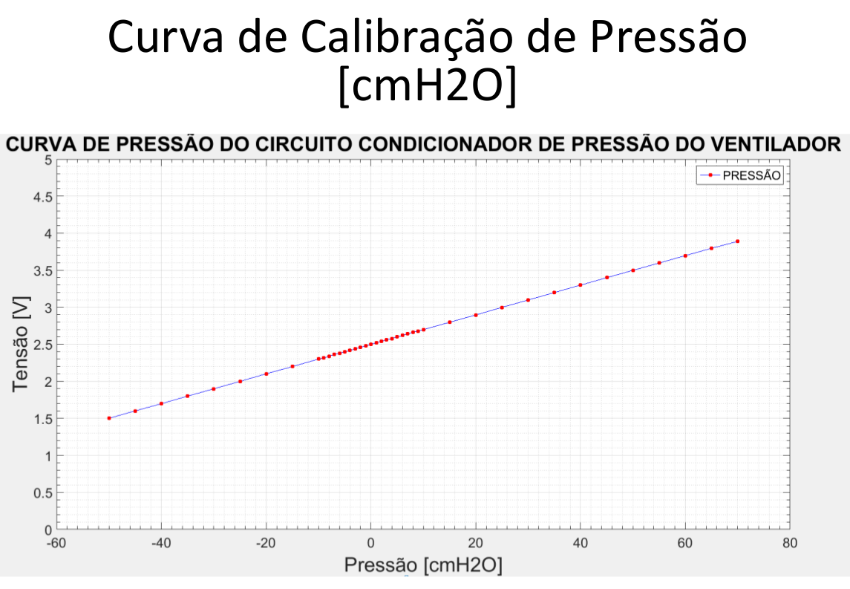
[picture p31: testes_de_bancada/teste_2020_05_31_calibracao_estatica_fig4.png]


## 6) Calibração Dinâmica (valores simulados)

Comparação das curvas de pressão e volume obtidas com um sensor de reverência (Analisador de Gases Fluke VT650) com as curvas de pressão obtidas com o simulador https://girardi.blumenau.ufsc.br/sdvm/, para os mesmos parâmetros ventilatórios.

## 7) Calibração Dinâmica (valores experimentais)

Comparação das curvas de pressão com um sensor de reverência, com as curvas de pressão efetivamente medidas com o sensor MPX5500DP. Obs: o analisador  Fluke aparentemente só exporta com uma frequência de amostragem máxima de 1Hz, o que não dá uma boa resolução das curvas. A solução seria usar o sensor Magnamed Ventmeter que tem interface RS232.

## 8) Determinação do procedimento de calibração do sensor de pressão embarcado

Estabelecer rotina de ajuste da calibração da medição de pressão. Procedimento de manutenção.

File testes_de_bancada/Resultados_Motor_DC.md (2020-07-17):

# Resultados dos testes com motor DC

- O motor DC foi avaliado por sua disponibilidade local, baixo custo e excelente torque em aplicações com redutores de rosca sem fim. 
- O uso do came permite ampliar a faixa de operação sem necessidade de inverter o sentido de rotação.
- Nas avaliações preliminares foi possível observar seu bom desempenho na função e produzindo pressão suficiente no AMBU.
- Com controles digitais foi possível ajustar os tempos de inspiração e expiração dentro de uma faixa relevante de operação.



- Embora na especificação estejam considerados MODOS VCV e/ou PCV alternativamente, a prática clínica protetiva aplicada aos pacientes de COVID tem sido executada exclusivamente em modo VCV.
- Embora o posicionamento do AMBU tenha se mostrado suficiente para controle da disponibilidade da mistura, o tempo inspiratório acabou sendo comprometido pelo limitado controle de velocidade.
- O volume também pôde ser controlado pelas válvulas de pressão. Neste caso, perde-se a mistura, eventualmente rica em Oxigênio.

### Alternativas

- Devido às dificuldades combinadas de controle de volume e faixa de tempos inspiratórios, decidiu-se explorar alternativa de atuadores com motor de passo e considerando reversão de direção de acionamento.
- Também é possível identificar aplicações para situações em que não há necessidade de Oxigênio e para ventilação protetiva em modo PCV.

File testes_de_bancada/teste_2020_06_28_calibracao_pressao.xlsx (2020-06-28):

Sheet: Planilha1
Ciclos | Posição | Válvula PEEP | Válvula VAP | Diferença | Vti (L) | Pulmão | Ciclos | Tempo I:E | Posição | Válvula PEEP | Válvula VAP | Diferença | Vti (L) | P fluke (cmH20) | P sensor (cmH2O)
18 | 0 | 5 | 10 | 5 | 0.297 | Mindray (P&B) | 35 | 1:01:00 | 0 | 5 | 10 | 5
18 | 0 | 5 | 20 | 15 | 0.557 | Mindray (P&B) | 35 | 1:01:00 | 0 | 5 | 20 | 15
18 | 0 | 5 | 30 | 25 | 0.733 | Mindray (P&B) | 35 | 1:01:00 | 0 | 5 | 30 | 25
18 | 0 | 5 | 40 | 35 | 0.834 | Mindray (P&B) | 35 | 1:01:00 | 0 | 5 | 40 | 35
18 | 0 | 10 | 10 | 0 | 0.289 | Mindray (P&B) | 35 | 1:01:00 | 0 | 10 | 10 | 0
18 | 0 | 10 | 20 | 10 | 0.499 | Mindray (P&B) | 35 | 1:01:00 | 0 | 10 | 20 | 10
18 | 0 | 10 | 30 | 20 | 0.645 | Mindray (P&B) | 35 | 1:01:00 | 0 | 10 | 30 | 20
18 | 0 | 10 | 40 | 30 | 0.690 | Mindray (P&B) | 35 | 1:01:00 | 0 | 10 | 40 | 30
18 | 0 | 15 | 20 | 5 | 0.4 | Mindray (P&B) | 35 | 1:01:00 | 0 | 15 | 20 | 5
18 | 0 | 15 | 30 | 15 | 0.462 | Mindray (P&B) | 35 | 1:01:00 | 0 | 15 | 30 | 15
18 | 0 | 15 | 40 | 25 | 0.58 | Mindray (P&B) | 35 | 1:01:00 | 0 | 15 | 40 | 25
18 | 0 | 20 | 20 | 0 | 0.507 | Mindray (P&B) | 35 | 1:01:00 | 0 | 20 | 20 | 0
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

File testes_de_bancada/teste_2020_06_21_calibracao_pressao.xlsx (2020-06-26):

Ciclos/min | Posição | Válvula PEEP [cmH2O] | Válvula VAP [cmH2O] | Driving Pressure (Diferença VAP – PEEP) | Vti (L) | Pulmão Artificial (modelo) | Ciclos/min | Tempo I:E | Posição | Válvula PEEP [cmH2O] | Válvula VAP [cmH2O] | Driving Pressure (Diferença VAP – PEEP) | Vti (L) | Pressão nas vias aéreas | Sensor Fluke [cmH20] | Pressão nas vias aéreas | Sensor AraPlus [cmH2O]
18 | 0 | 5 | 10 | 5 | 0.297 | Mindray (P&B) | 35 | 1:01:00 | 0 | 5 | 10 | 5
18 | 0 | 5 | 20 | 15 | 0.557 | Mindray (P&B) | 35 | 1:01:00 | 0 | 5 | 20 | 15
18 | 0 | 5 | 30 | 25 | 0.733 | Mindray (P&B) | 35 | 1:01:00 | 0 | 5 | 30 | 25
18 | 0 | 5 | 40 | 35 | 0.834 | Mindray (P&B) | 35 | 1:01:00 | 0 | 5 | 40 | 35
18 | 0 | 10 | 10 | 0 | 0.289 | Mindray (P&B) | 35 | 1:01:00 | 0 | 10 | 10 | 0
18 | 0 | 10 | 20 | 10 | 0.499 | Mindray (P&B) | 35 | 1:01:00 | 0 | 10 | 20 | 10
18 | 0 | 10 | 30 | 20 | 0.645 | Mindray (P&B) | 35 | 1:01:00 | 0 | 10 | 30 | 20
18 | 0 | 10 | 40 | 30 | 0.690 | Mindray (P&B) | 35 | 1:01:00 | 0 | 10 | 40 | 30
18 | 0 | 15 | 20 | 5 | 0.4 | Mindray (P&B) | 35 | 1:01:00 | 0 | 15 | 20 | 5
18 | 0 | 15 | 30 | 15 | 0.462 | Mindray (P&B) | 35 | 1:01:00 | 0 | 15 | 30 | 15
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

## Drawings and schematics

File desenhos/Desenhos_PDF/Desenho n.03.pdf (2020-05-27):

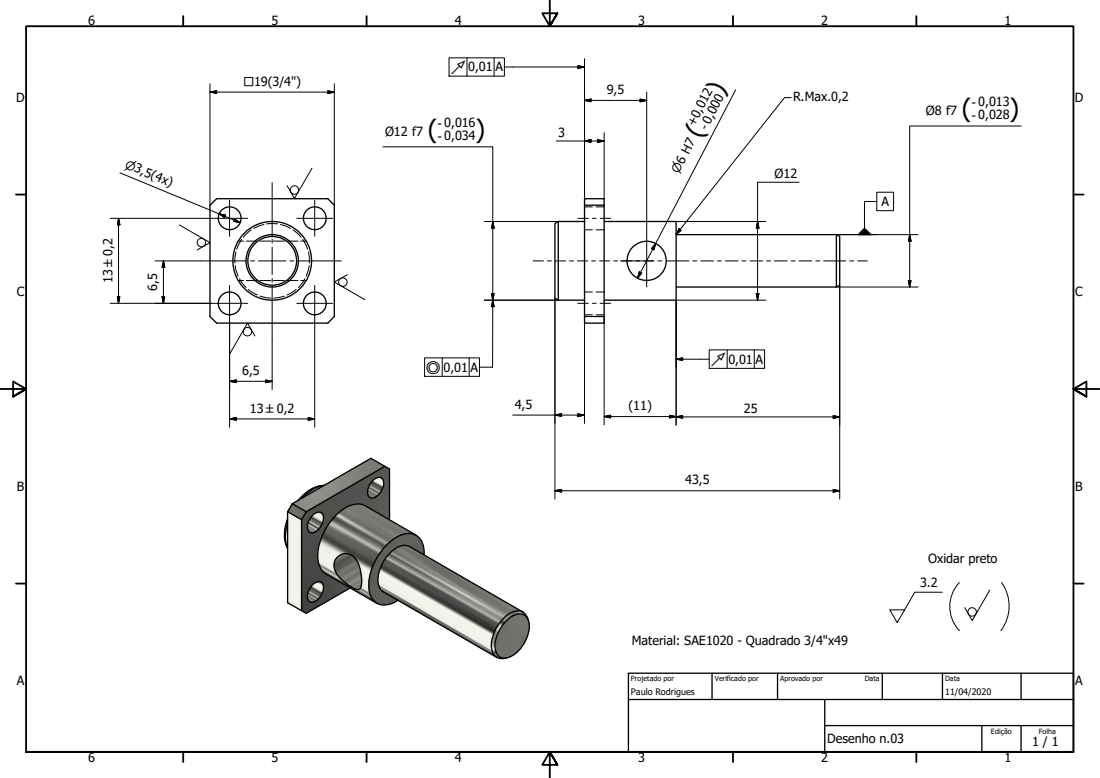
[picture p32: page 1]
Desenho n.03; Paulo Rodrigues; Projetado por; Verificado por; Aprovado por; Data; Oxidar preto; Material: SAE1020 - Quadrado 3/4"x49

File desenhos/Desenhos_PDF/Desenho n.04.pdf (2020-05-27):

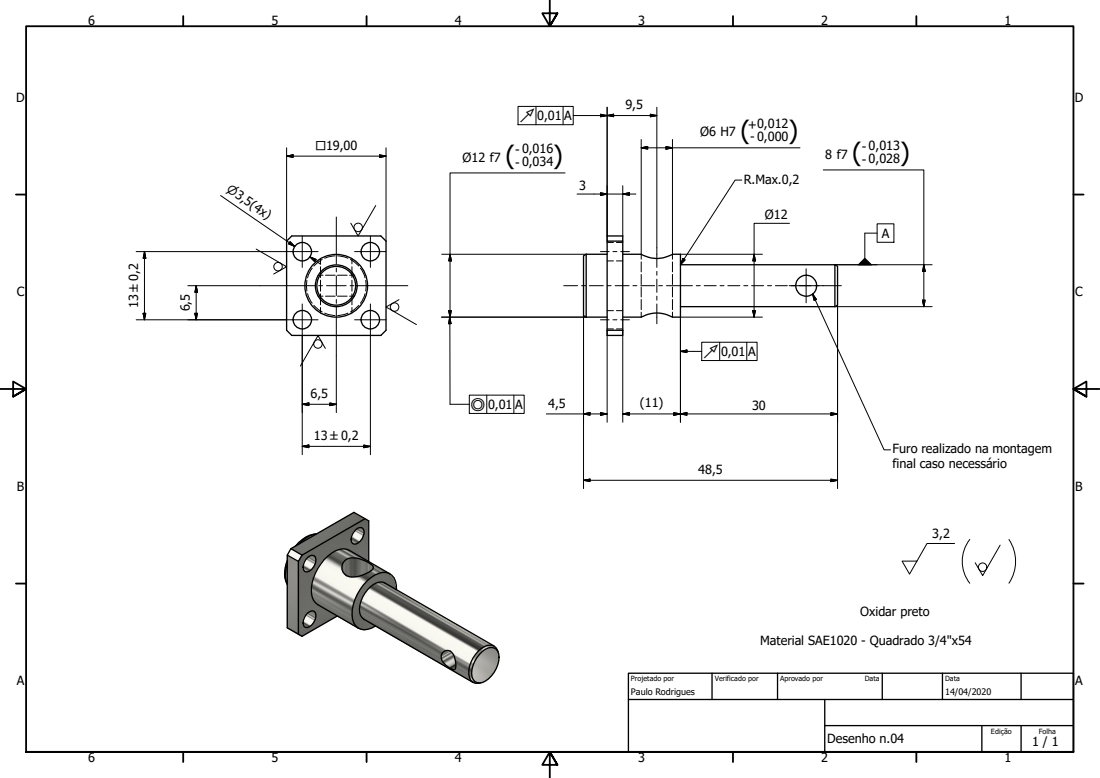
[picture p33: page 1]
Desenho n.04; Paulo Rodrigues; Projetado por; Verificado por; Aprovado por; Data; Oxidar preto; Material SAE1020 - Quadrado 3/4"x54

Furo realizado na montagem
final caso necessirio

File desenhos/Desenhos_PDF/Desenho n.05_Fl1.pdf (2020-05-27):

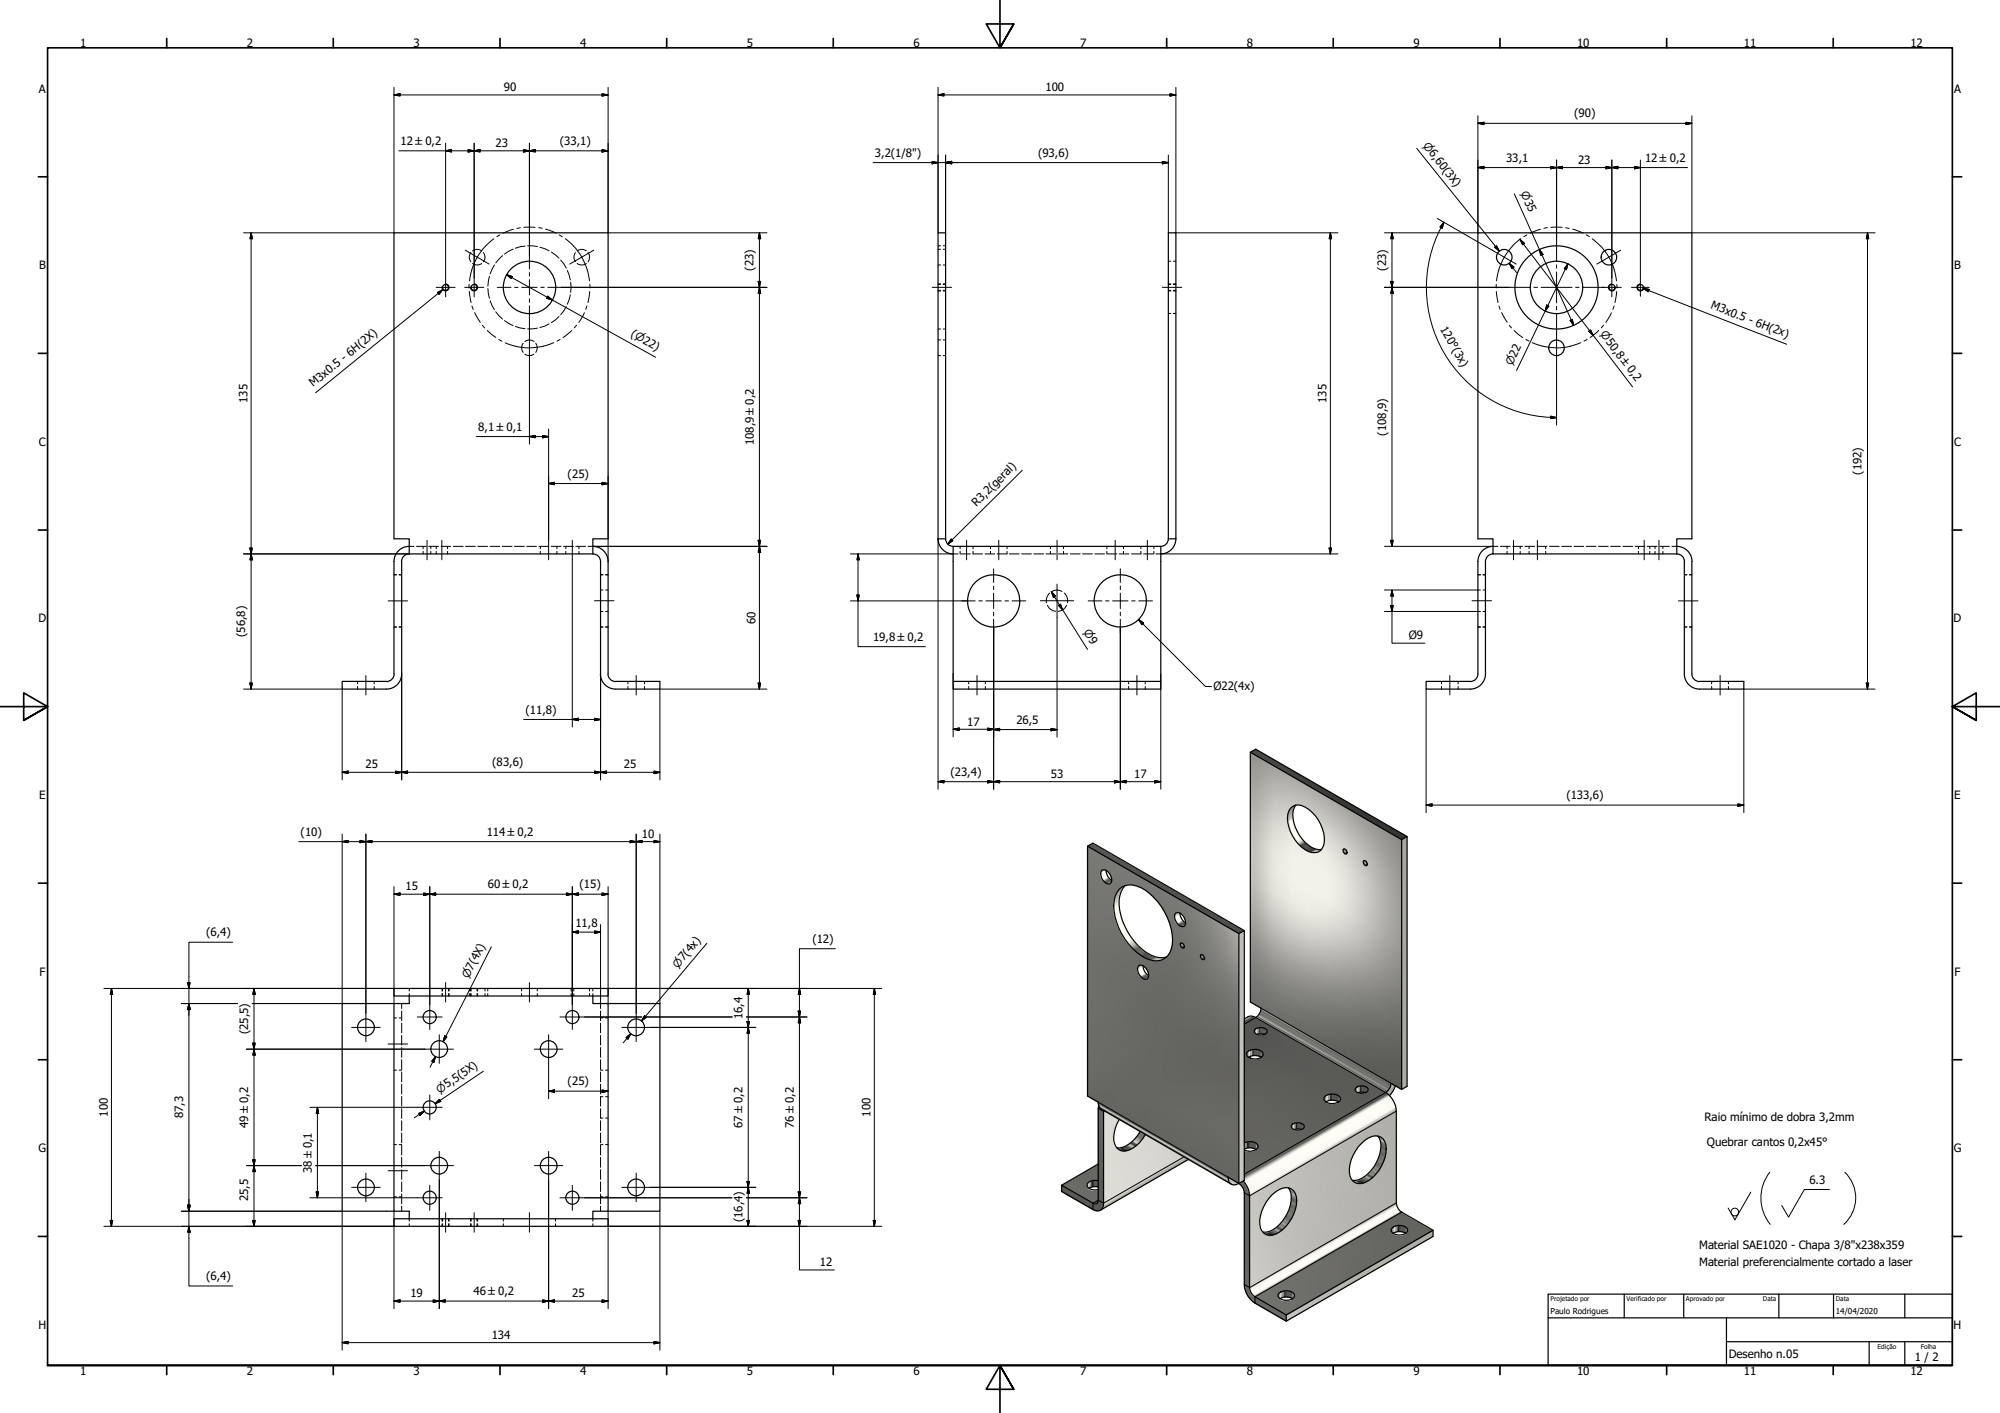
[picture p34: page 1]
Desenho n.05; Paulo Rodrigues; Projetado por; Verificado por; Aprovado por; Data; Quebrar cantos 0,2x45°

Raio mtnimo de dobra 3,2mm

Material SAE1020 - Chapa 3/8"x238x359
Material preferencialmente cortado a laser

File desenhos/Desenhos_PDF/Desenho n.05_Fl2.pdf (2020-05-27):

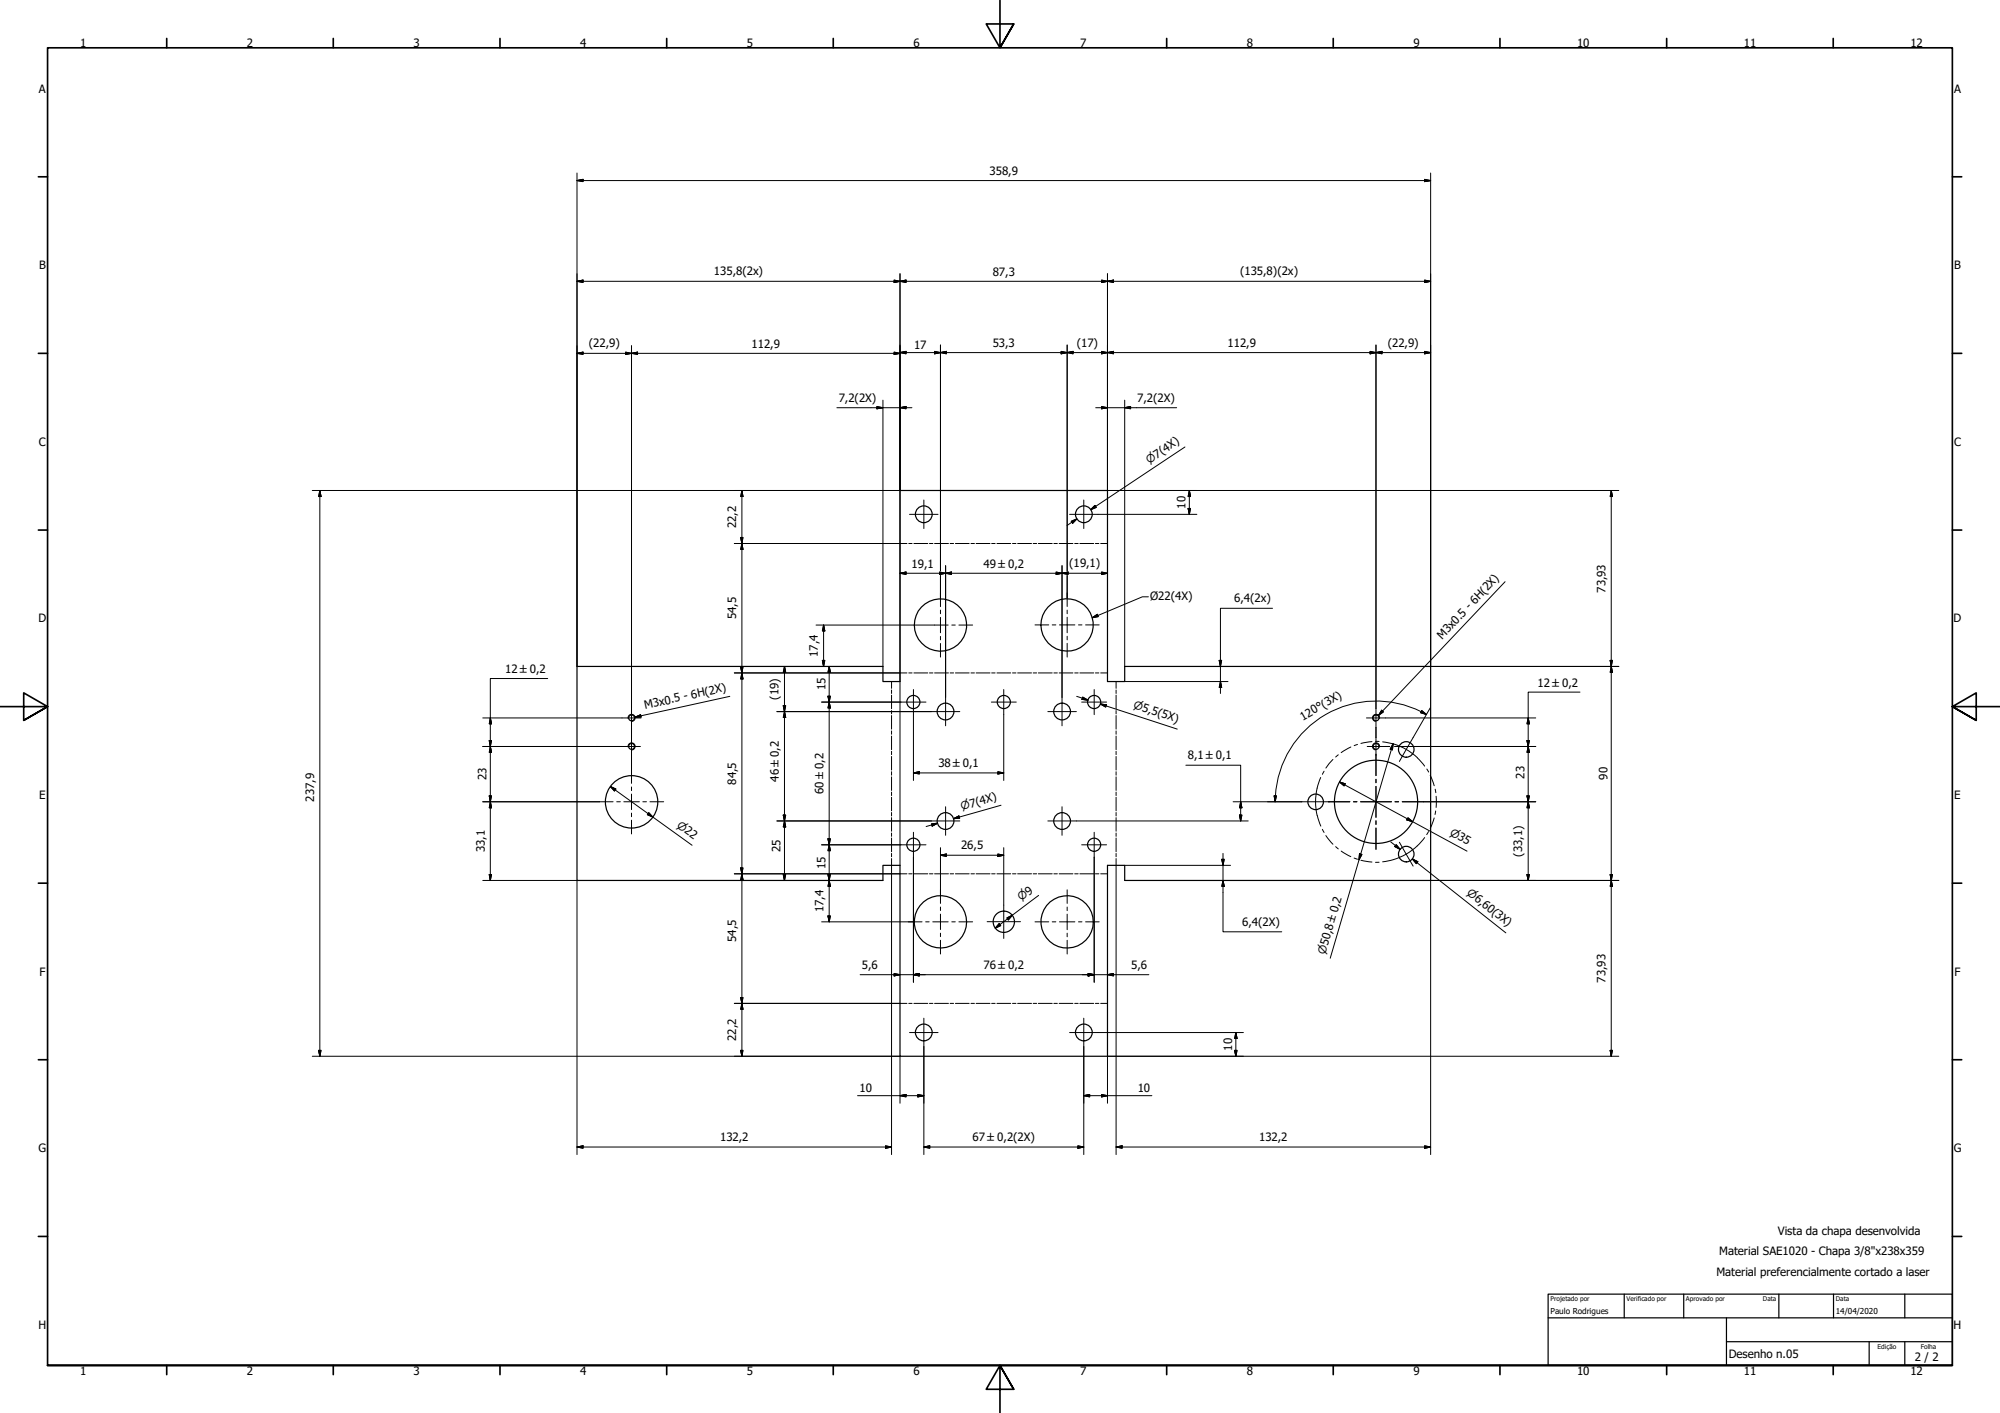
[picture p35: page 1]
Desenho n.05; Paulo Rodrigues; Projetado por; Verificado por; Aprovado por; Data

Vista da chapa desenvolvida

Material SAE1020 - Chapa 3/8"x238x359
Material preferencialmente cortado a laser

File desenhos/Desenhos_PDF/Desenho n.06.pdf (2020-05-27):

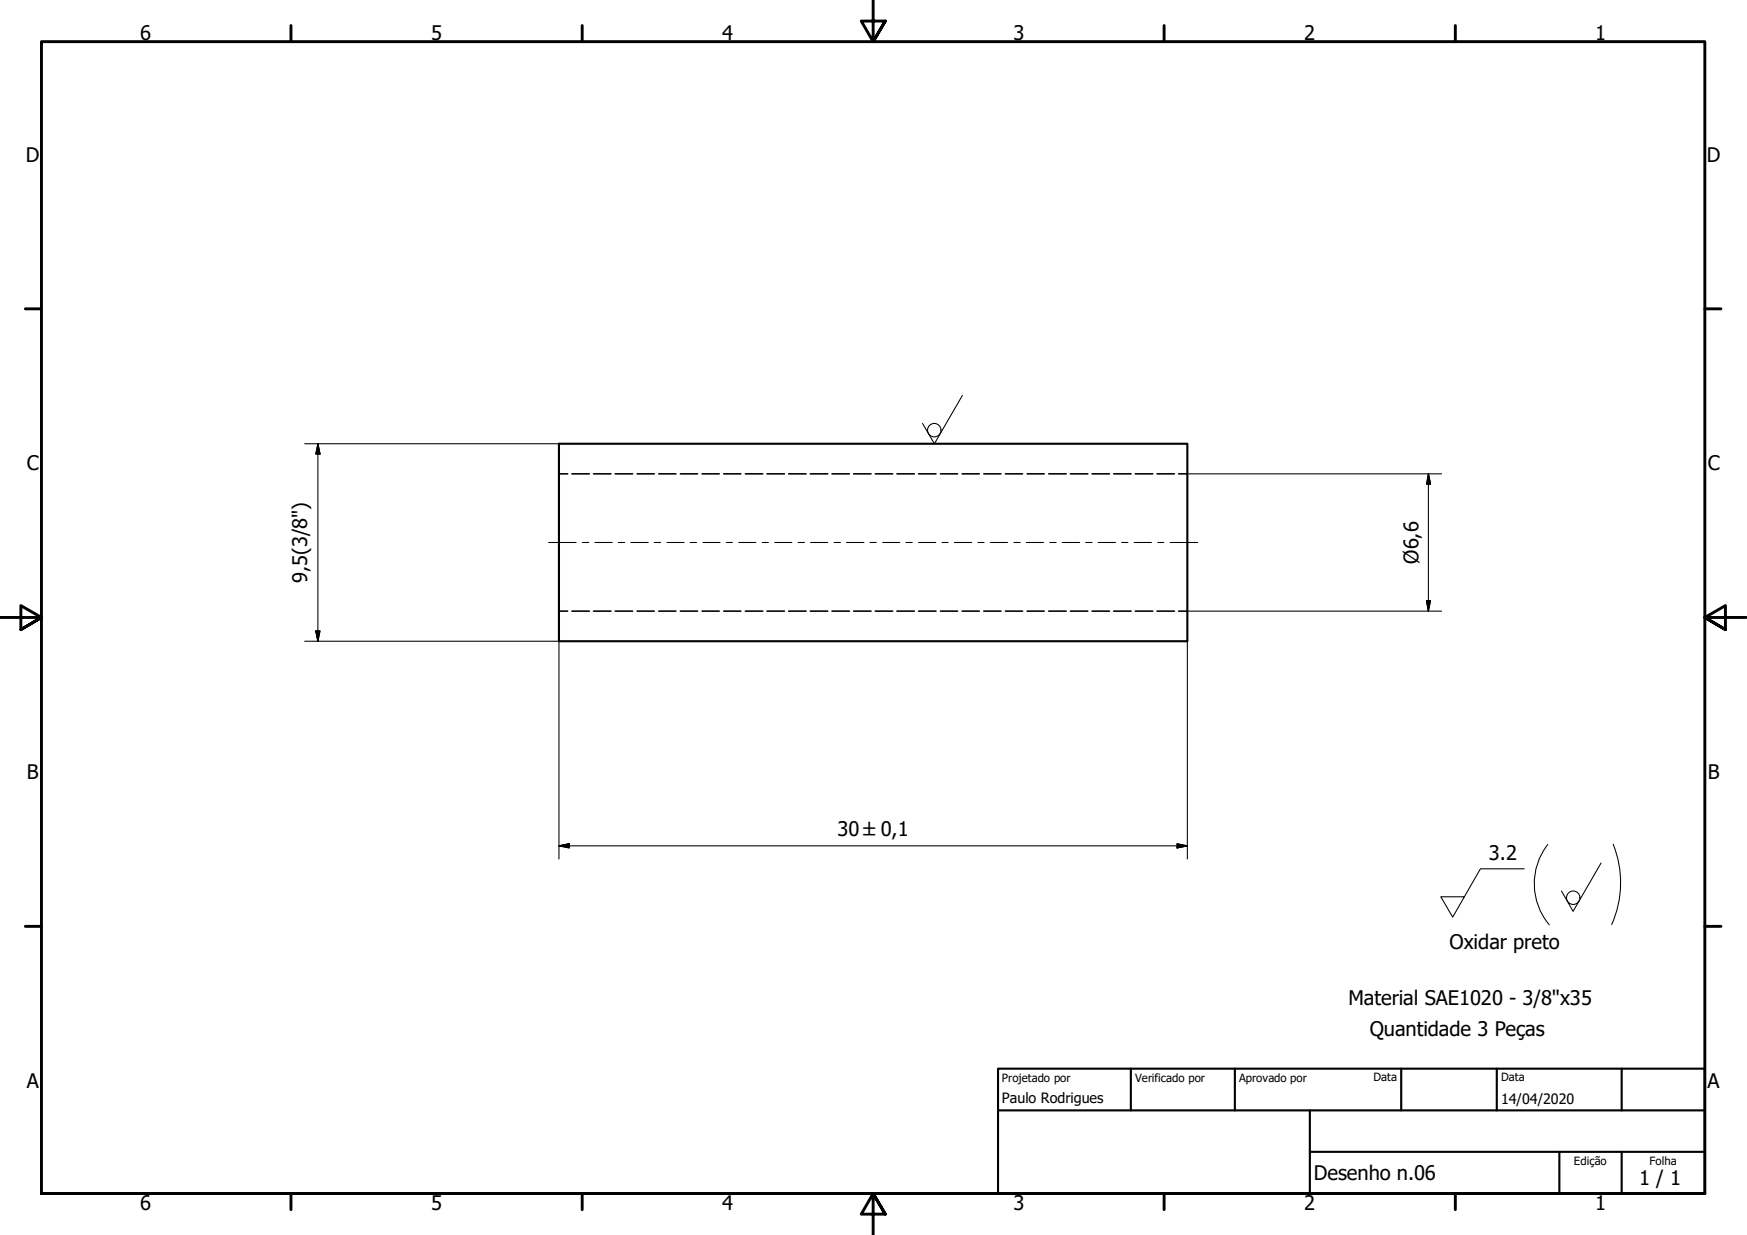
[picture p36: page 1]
Desenho n.06; Paulo Rodrigues; Projetado por; Verificado por; Aprovado por; Data; Oxidar preto; Material SAE1020 - 3/8"x35; Quantidade 3 Peoas

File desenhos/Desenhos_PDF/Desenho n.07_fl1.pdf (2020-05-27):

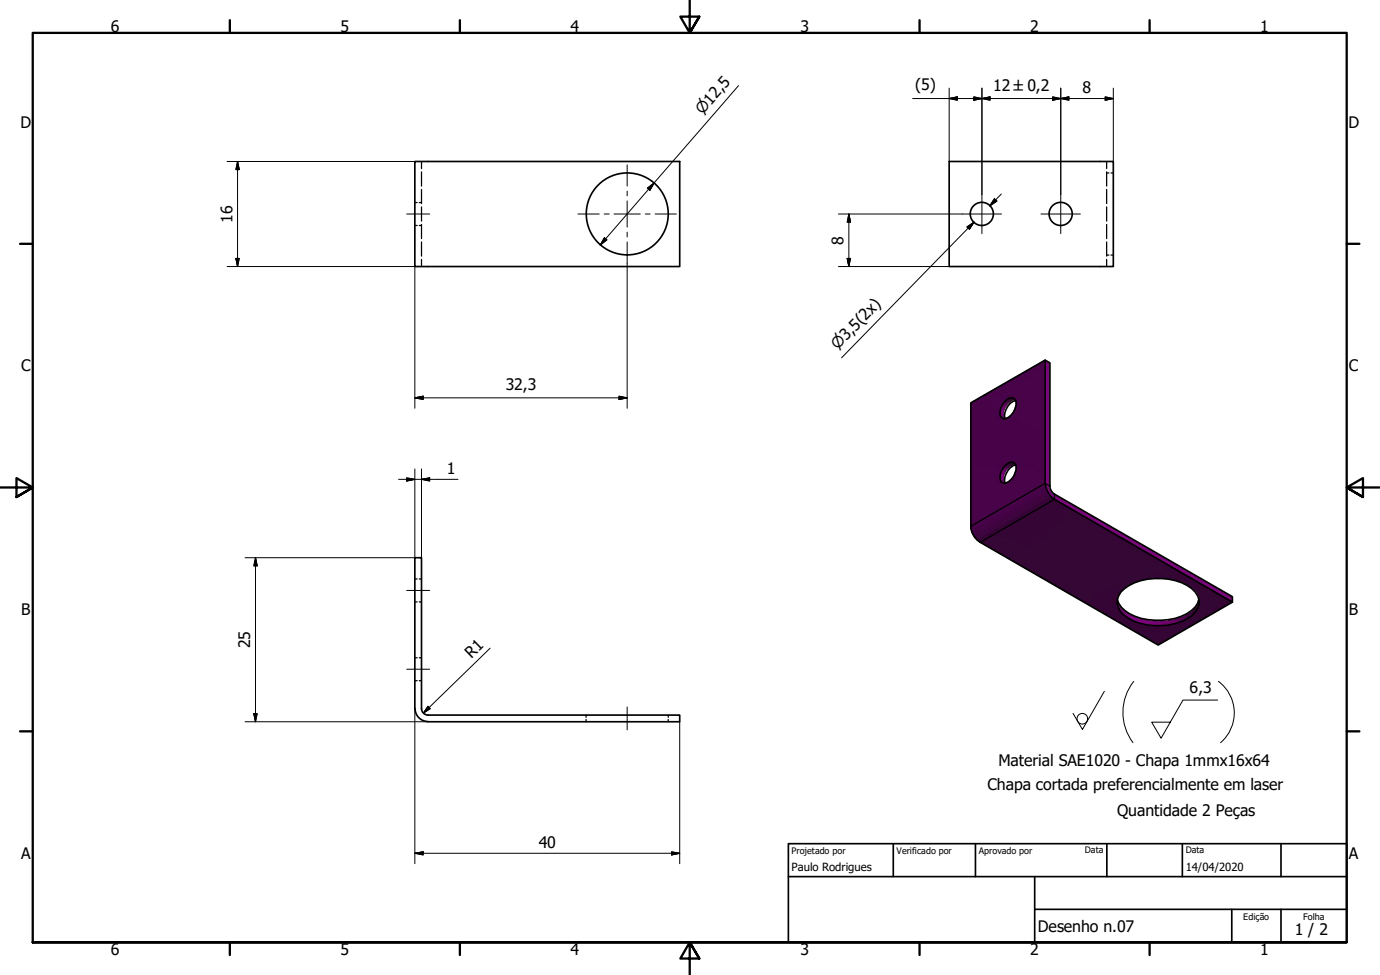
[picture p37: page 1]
Desenho n.07; Paulo Rodrigues; Projetado por; Verificado por; Aprovado por; Data; Quantidade 2 Peoas

Material SAE1020 - Chapa 1mmx16x64
Chapa cortada preferencialmente em laser

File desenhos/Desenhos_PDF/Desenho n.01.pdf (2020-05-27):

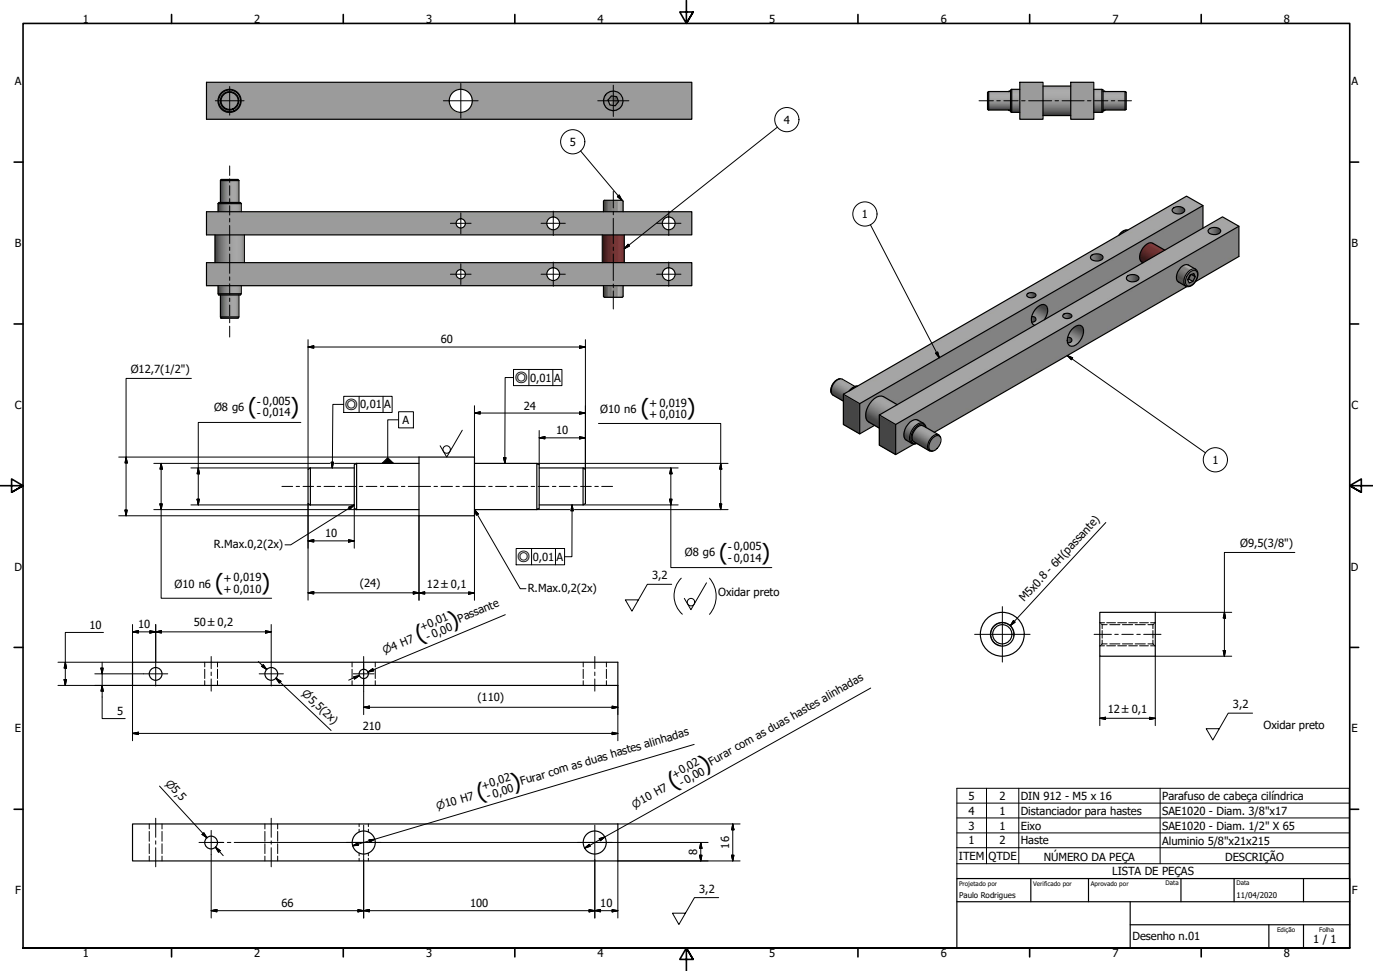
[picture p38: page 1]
Desenho n.01; Paulo Rodrigues; Projetado por; Verificado por; Aprovado por; Data; M5x0.8 - 6H(passante); Oxidar preto; (24) R.Max.0,2(2x)

)Furar com as duas hastes alinhadas

5 | 2 | DIN 912 - M5 x 16 | Parafuso de cabeoa ciltndrica
4 | 1 | Distanciador para hastes | SAE1020 - Diam. 3/8"x17
3 | 1 | Eixo | SAE1020 - Diam. 1/2" X 65
1 | 2 | Haste | Aluminio 5/8"x21x215
ITEM | QTDE | NÒMERO DA PEdA | DESCRId-O

LISTA DE PEdAS

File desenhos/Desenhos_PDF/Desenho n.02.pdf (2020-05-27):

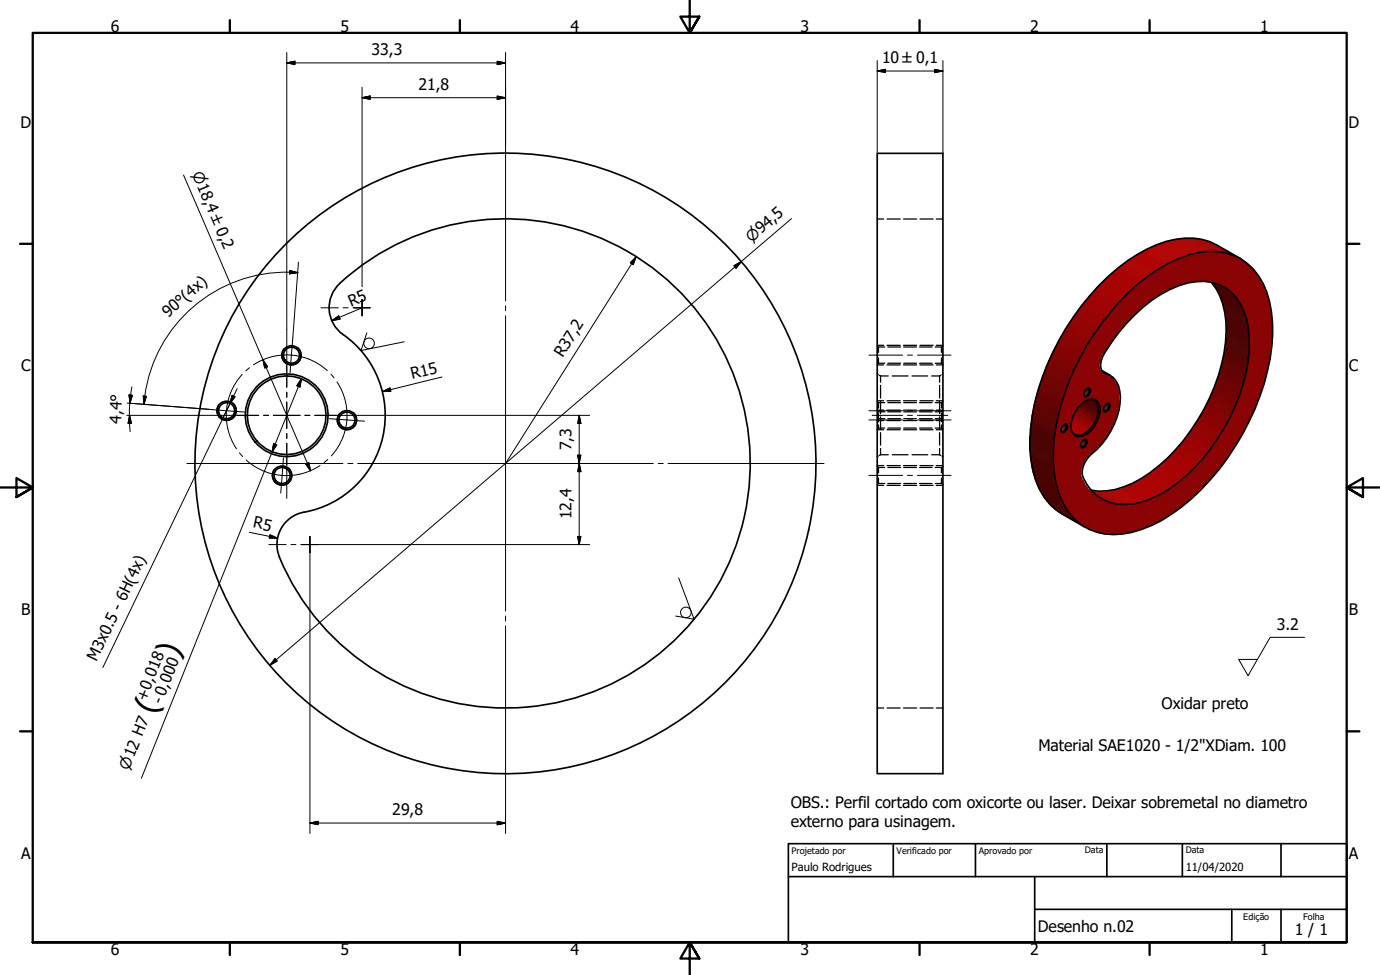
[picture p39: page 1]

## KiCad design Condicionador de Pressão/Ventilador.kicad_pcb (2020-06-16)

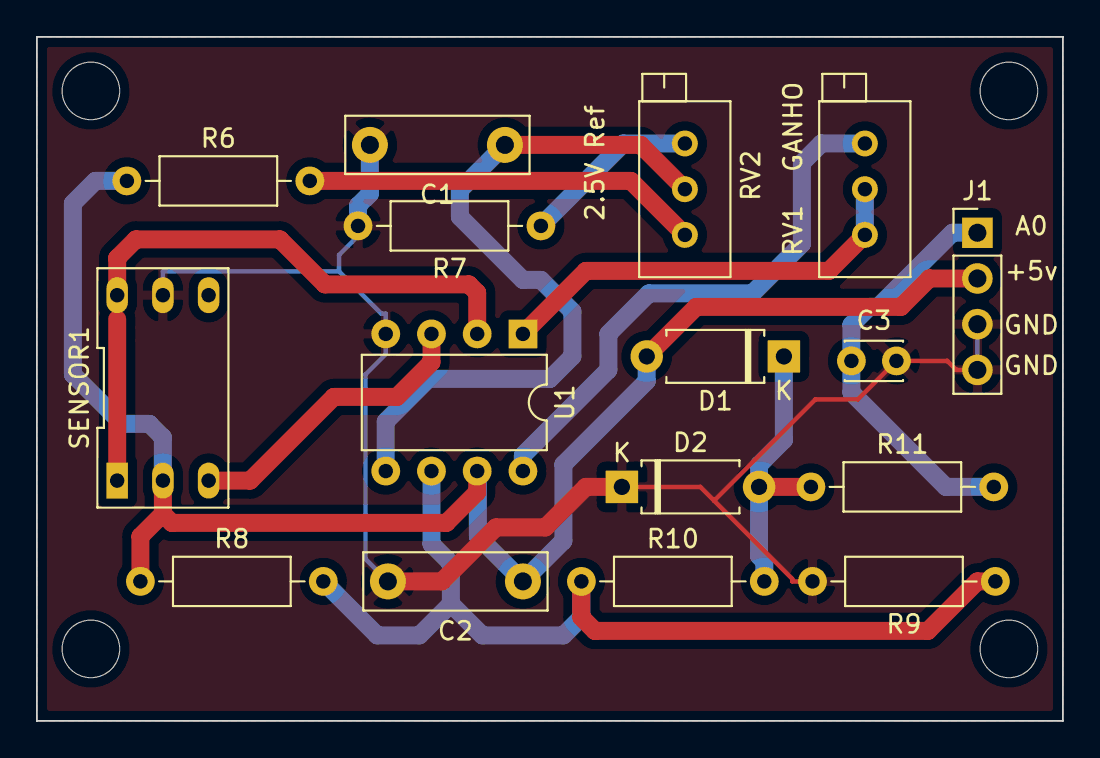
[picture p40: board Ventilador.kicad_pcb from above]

Board: 2 copper layers, 57.0 x 38.0 mm, 16 parts (0 on the bottom side), 12 nets.

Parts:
C1, C2: 100nF; C_Rect_L10.0mm_W3.0mm_P7.50mm_MKS4
C3: 200pF; C_Disc_D3.0mm_W2.0mm_P2.50mm
D1, D2: DIODE; D_A-405_P7.62mm_Horizontal
J1: Conn_01x04_Male; PinHeader_1x04_P2.54mm_Vertical
R6, R7: 3,3k; R_Axial_DIN0207_L6.3mm_D2.5mm_P10.16mm_Horizontal
R8, R9: 10k; R_Axial_DIN0207_L6.3mm_D2.5mm_P10.16mm_Horizontal
R10: 100R; R_Axial_DIN0207_L6.3mm_D2.5mm_P10.16mm_Horizontal
R11: 6,8k; R_Axial_DIN0207_L6.3mm_D2.5mm_P10.16mm_Horizontal
RV1: 1k; Potentiometer_Bourns_3296X_Horizontal
RV2: 2k; Potentiometer_Bourns_3296X_Horizontal
SENSOR1: MPS20N0040d-S; DIP-6_405_ELL
U1: INA128; DIP-8_W7.62mm

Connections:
+5V: C2.1, D1.2, J1.2, R6.1, R8.1, SENSOR1.2, U1.7
A0: C3.1, J1.1, R11.2
GND: C1.2, C2.2, C3.2, D2.1, J1.3, J1.4, R7.2, R9.2, SENSOR1.5, U1.4
unnamed: C1.1, RV2.2, U1.5
unnamed: D1.1, D2.2, R10.2, R11.1
unnamed: R6.2, RV2.1
unnamed: R7.1, RV2.3
unnamed: R8.2, R9.1, R10.1, U1.6
unnamed: RV1.1, RV1.2, U1.1
unnamed: RV1.3, U1.8
unnamed: SENSOR1.1, SENSOR1.6, U1.2
unnamed: SENSOR1.3, U1.3

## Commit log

2020-04-23 3D Printed Pieces
2020-05-22 Lista de compras, materiais e glossário
    Criação dos campos lista de compras, lista de materiais e glossário para ser preencido posteriormente
2020-05-27 Adição de pasta com desenhos em pdf e dwg. Adição de pasta com os editais UFABC e IEEE e do projeto submetido para o edital UFABC.
    [#Desenho n.05_fl1_Folha_1.dwg, Desenho n.05_fl1_Folha_1.dwg, Desenho n.05_fl1_Folha_2.dwg, Desenho n.07_fl1_Folha_1.dwg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]
2020-05-27 Criação da pagina DESENHOS.md para dar detalhes sobre os desenhos de fabricação das partes mecânicas.
2020-05-27 Links para pastas desenhos e pasta editais.
    Links para pastas desenhos e pasta editais. E ainda modificações em hiperlinks da Equipe e mais informações do glossário
2020-06-07 Propostas circuito pneumatico
    Propostas circuito pneumatico e atualização da cronologia com edital IEEE e
2020-06-07 Imagens das propostas do circuito pneumatico
2020-06-16 Atualização de Repositório
    [Ventilador.dsn, Ventilador.kicad_pcb, Ventilador.sch, Ventilador_V1.dsn]
2020-06-19 Projeto IEEE submetido
    Documento contém apenas a transcrição do formulário online que foi submetido
2020-06-19 Projeto submetido para edital IEEE
    O arquivo é uma transcrição do texto preenchido no formulário online.
2020-06-21 Testes Funcionais de Bancada
    Criação da seção "Descrição dos Testes Funcionais de Bancada (in vitro)"
2020-06-26 Criação de pasta com descrição de testes em bancada
    [teste_2020_06_21_calibracao_pressao.xlsx]
2020-06-27 Complementação de info sobre experimento apos conversa com Roberto Assano
2020-06-27 Eliminei ###Resultados para melhor clareza
2020-06-27 Update TESTES_DE_BANCADA.md
    Retomados os itens 2 e 6 que estavam no README e foram perdidos na criação desta página
2020-06-28 Criando arquivo dos testes mas ainda sem dados
    [teste_2020_06_28_calibracao_pressao.xlsx]
